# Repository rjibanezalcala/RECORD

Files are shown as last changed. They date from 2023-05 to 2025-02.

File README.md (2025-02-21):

# Welcome to RECORD!
The the REward-COst in Rodent Decision-making (RECORD) is a microcontroller-based system for the design and implementation of behavioural trials with the ability to synchronise with other external neural recording systems. RECORD has a variety of applications, but its main purpose is for behavioural neuroscience implementations.

The system offers modularity and customisability at its core. It includes 3D-printed components, electronics, and software.

[Check out our published paper on Nature Communications Biology!](https://doi.org/10.1038/s42003-024-06489-8)

## 3D printing
We have personally designed every 3D-printed component of the system, and have provided the [AutoCAD files](https://github.com/rjibanezalcala/RECORD/tree/main/3d-prints/cad) for editing, and the [STL files](https://github.com/rjibanezalcala/RECORD/tree/main/3d-prints/stl) for printing directly. 

## Electronic hardware and firmware
The electronics that drive the RECORD system are cheap but effective. We use an embedded systems approach to allow for customisable trials that can either be automated, or performed manually. The embedded electronics work on a command-servicing routine, which will make the electronics react to commands sent by the user via serial communications.

We chose the [Texas Instruments MSP430-FR2355 microcontroller](https://www.ti.com/tool/MSP-EXP430FR2355) due to its low price (~13 USD) and versatility. All of RECORD's [microcontroller firmware](https://github.com/rjibanezalcala/RECORD/tree/main/microcontroller) can be found within this repository.

Our custom-designed PCB is a hub for signals to be relayed from the microcontroller to our rodent arenas. We provide all [Gerber files](https://github.com/rjibanezalcala/RECORD/tree/main/pcb) in this repository.

## Software
Within this repository, you will find example scripts and workflows that can be used as templates for designing your own behavioural trials. For example, we have developed software packages designed specifically for our system. These packages allow scripting of customised trials in [Python](https://github.com/rjibanezalcala/RECORD/tree/main/python). We also provide [Ethovision experiments](https://github.com/rjibanezalcala/RECORD/tree/main/ethovision_experiments) and [Bonsai workflows](https://github.com/rjibanezalcala/RECORD/tree/main/bonsai_workflows) containing our custom decision making task.

Specifically for Ethovision, we provided [Batch scripts](https://github.com/rjibanezalcala/RECORD/tree/main/microcontroller/batch_scripts) that allow communication with our microcontroller system within an experiment's trial-control.

Data management is important for high-throughput systems, thus we created [Serendipity](https://github.com/lddavila/UTEP-Brain-Computation-Lab-Remote-Databases-and-Serendipity-App/tree/main/App%20Deployment%20Folder), a databasing and data pre-processing software suite, provided in an outside repository.

Finally, our data analysis software suite, including [behavioural feature extraction tools](https://github.com/atanugiri/Feature-Extraction), [neuroeconomic analysis tools](https://github.com/rjibanezalcala/RECORD/tree/main/data_analysis/neuroeconomic_analysis), [behavioural classification tools](https://github.com/lddavila/UTEP-Brain-Computation-Lab-Remote-Databases-and-Serendipity-App), are all provided within this and outside repositories.

trial_start_tone was created using [Tonegen](https://www.nch.com.au/tonegen/index.html).

## Documentation

The User Manual, Build guides, and other documentation can be found in our [documentation](https://github.com/rjibanezalcala/RECORD/tree/main/documentation) section.
<!--
> Written with [StackEdit](https://stackedit.io/).
-->
<!--stackedit_data:
eyJoaXN0b3J5IjpbMTIzNTUwMDI1Nl19
-->

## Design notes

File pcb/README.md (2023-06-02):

# Welcome to RECORD/pcb!
Our custom PCB was designed using [Autodesk EAGLE](http://eagle.autodesk.com/). We have provided our projects as a Zip file for importing into EAGLE and making modifications, as well as the Gerber files we used for printing the board. 
## Our custom Printed Circuit Board (PCB)
The printed circuit board serves as a relay center for the various signals that the RECORD hardware needs for function. It also houses various JST connectors to ensure secure connection of the different cable assemblies. Every component on the PCB is through-hole, useful for manual soldering of each component. 
## Resistor values
Resistor values depend mostly on the LEDs chosen for the system. They are mainly for stepping a higher voltage signal down for protection of the LEDs. The voltage divider section is used for protection of the microcontroller, in case input TTL signals cannot be adjusted to the microcontroller's operating range.

> Written with [StackEdit](https://stackedit.io/).
<!--stackedit_data:
eyJoaXN0b3J5IjpbMzA1NjkyMDExLDQxMzA1NjI3NF19
-->

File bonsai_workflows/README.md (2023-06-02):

# Welcome to RECORD/bonsai_workflows!
[Bonsai](https://bonsai-rx.org/) is a visual programming interface that is useful for multiple applications across various fields. Herein, we include the workflows (visual code) we have used for interfacing with [our Basler cameras](https://www.baslerweb.com/en/products/cameras/area-scan-cameras/ace/aca1300-60gc/) for the purpose of tracking an animal's location on the RECORD arenas. 
## Workflow dependencies
This is a list of dependencies that are needed for our workflows. Bolded are the libraries that are absolutely essential. You can install libraries directly from Bonsai using the *Bonsai Gallery*.
1. Bonsai - Core Library
2. Bonsai - Design Library
3. Bonsai - Visualizers Library
4. **Bonsai - Dsp Library**
5. Bonsai - Dsp Design Library
6. Bonsai - Editor
7. **Bonsai - Pylon Library**
8. **Bonsai - Scripting Library**
9. Bonsai - Expression Scripting Library
10. **Bonsai - Starter Pack**
11. **Bonsai - Vision Library** 
12. Bonsai - Vision Design Library
## Basler GigE camera interface
To use Bonsai with a Basler GigE camera, you'll need a software interface that essentially provides Bonsai with the information needed to operate the camera. We recommend Basler's [Pylon Viewer](https://www.baslerweb.com/en/downloads/software-downloads/software-pylon-7-3-0-windows/) for this purpose. After setting up the camera, make sure to export the camera features to a file and feed that to the camera capture node in the "Live rat tracking" workflow contained here.

> Written with [StackEdit](https://stackedit.io/).
<!--stackedit_data:
eyJoaXN0b3J5IjpbLTg0MjU0MDEyM119
-->

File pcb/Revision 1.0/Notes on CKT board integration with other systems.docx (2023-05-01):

### Electrophysiology

### Optogenetics (Behaviour Manipulation)

- Outgoing microcontroller TTL signal was not strong enough to drive both the Prizmatix pulser and the indicator LED (ACK1, SYNC1, ACK2, or SYNC2) circuit.
  - Disconnected LED circuit and the 3.3V TTL was able to drive the pulser.

### Optogenetics (Calcium Imaging)

- The Incopix DAQ box can control the output voltage of its TTLs
  - Set this voltage to 3.3V to avoid damaging the indicator LEDs (ACK1, SYNC1, ACK2, or SYNC2) and microcontroller input.

Raquel Ibáñez Alcalá Created 27 September, 2022 for PCB rev.1.0

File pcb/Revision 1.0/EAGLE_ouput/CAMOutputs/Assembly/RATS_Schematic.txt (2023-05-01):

Partlist exported from R:/Data/Raylene/Documents/EAGLE/projects/FriedmanLab_RATS PCB/RATS_Schematic.sch at 20-Dec-21 21:25

Qty Value             Device            Package                    Parts                                             Description               COPYRIGHT                                                MANUFACTURER_PART_NUMBER MF MFR_NAME MPN OC_FARNELL OC_NEWARK POPULARITY SPICEPREFIX
10                    R-EU_0204/7       0204/7                     R1, R2, R3, R4, R5, R6, R7, R8, R9, R10           RESISTOR, European symbol                                                                                                                        79         R          
12  1N4004            1N4004            DO41-10                    D1, D2, D3, D4, D5, D6, D7, D8, D9, D10, D11, D12 DIODE                                                                                                                                            82                    
4   3.3V              LED5MM            LED5MM                     ACK1, ACK2, SYNC1, SYNC2                          LED                                                                                                                                              93                    
1   ACK1_J            JP1E              JP1                        JP1                                               JUMPER                                                                                                                                           61                    
1   ACK2_J            JP1E              JP1                        JP3                                               JUMPER                                                                                                                                           61                    
4   B2B-XH-A(LF)(SN)  B2B-XH-A(LF)(SN)  CONN_B2B-XH-A(LF)(SN)_JST  TTL/SYNC1, TTL/SYNC2, VALVE_PWR1, VALVE_PWR2                                Copyright (C) 2021 Ultra Librarian. All rights reserved. B2B-XH-A(LF)(SN)            JST                                                     
4   B4B-XH-A_(LF)(SN) B4B-XH-A_(LF)(SN) CONN_B4B-XH-A_(LF)(SN)_JST RELAY_IN1, RELAY_IN2, RELAY_POWER1, RELAY_POWER2                            Copyright (C) 2021 Ultra Librarian. All rights reserved. B4B-XH-A (LF)(SN)           JST                                                     
2   B5B-XH-A(LF)(SN)  B5B-XH-A(LF)(SN)  CONN_B5B-XH-A(LF)(SN)_JST  VALVE_OUT1, VALVE_OUT2                                                      Copyright (C) 2021 Ultra Librarian. All rights reserved. B5B-XH-A(LF)(SN)            JST                                                     
2   B6B-XH-A(LF)(SN)  B6B-XH-A(LF)(SN)  CONN_B6B-XH-A(LF)(SN)_JST  LED_OUT1, LED_OUT2                                                          Copyright (C) 2021 Ultra Librarian. All rights reserved. B6B-XH-A(LF)(SN)            JST                                                     
1   MCU_LED/PWM1      FE05-1            FE05-1                     H5                                                FEMALE HEADER                                                                                                               unknown    unknown   7                     
1   MCU_LED/PWM2      FE05-1            FE05-1                     H6                                                FEMALE HEADER                                                                                                               unknown    unknown   7                     
1   MCU_RELAY         FE08-1            FE08                       H3                                                FEMALE HEADER                                                                                                               unknown    unknown   10                    
1   MCU_TTL           FE05-1            FE05-1                     H2                                                FEMALE HEADER                                                                                                               unknown    unknown   7                     
1   MCU_VCC/GND       FE05-1            FE05-1                     H1                                                FEMALE HEADER                                                                                                               unknown    unknown   7                     
1   RELAY_POWERSEL    JP3Q              JP3Q                       JP5                                               JUMPER                                                                                                                                           5                     
1   RELAY_TRIG        FE10-1            FE10                       H4                                                FEMALE HEADER                                                                                                               unknown    unknown   4                     
1   SYNC1_J           JP1E              JP1                        JP2                                               JUMPER                                                                                                                                           61                    
1   SYNC2_J           JP1E              JP1                        JP4                                               JUMPER                                                                                                                                           61                    
1   VDIVSEL1          JP2E              JP2                        JP6                                               JUMPER                                                                                                                                           34                    
1   VDIVSEL2          JP2E              JP2                        JP7                                               JUMPER                                                                                                                                           34

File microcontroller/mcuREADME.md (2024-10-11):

# Welcome to RECORD/microcontroller!
The code in this repository was written for the [MSP430-FR2355 microcontroller development kit](https://www.ti.com/tool/MSP-EXP430FR2355) in [Texas Instrument's Code Composer Studio 11.1.0](https://www.ti.com/tool/download/CCSTUDIO/11.1.0.00011).

# Firmware
This repository contains 3 files:

 1. 'main.c' file: The microcontroller firmware. This code is essential for the functionality of the microcontroller system and will call the other two files. It contains setup and initialisation, the command servicing routine, interrupt servicing routines, and main variable definitions.
 2. 'RECORD.h' file: A header file containing essential variables and functions necessary for functionality.
 3. 'mcucfg.h' file: A header file referenced by the 'RECORD.h' file that defines default parametres loaded by the microcontroller at startup.
	 - This file contains variables essential to the brightness of the cost lights, as they will control the pulse width-modulated signal that turns on the cost lights.  **Make sure these values are calibrated to your setup's specific needs!**
 
 These three files must be flashed to the microcontroller in order for the RECORD system to work. The 'mcucfg.h' file may be named something else and multiple copies can be made for a setup using multiple RECORD arenas, however, make sure that the 'RECORD.h' file references the correct 'cfg' file when flashing.

## A note on HARP compliance
RECORD firmware is currently not [HARP](https://harp-tech.org/) compliant, however, we are working on this and will be adding HARP compatibility in a future release!

# Updates
A rundown of the current version's most recent changes will be shown here!

## Current version v2.2.0 (17/February/2022) 
### Firmware:
 1. Added the capability to switch TTL operation modes by configuring in configuration mode
	 - TOGGLE will turn the TTL on and keep it on until it is toggled again
	 -  PULSE is the legacy mode, only stays on for as long as TTL_LENGTH
	   indicates, then turns back off. 
	 - OFF is off, duh!
 2. TTL OUT command ‘T’ will now check for the TTL operation mode and act accordingly.
 3. Information mode ('?' command):
	- Will now report the operation mode of the output TTL immediately before reporting CCR values.
	- Will now prompt the user to either enter H to display the help section, or Enter to exit info mode. Any character sent will also exit info mode.
 4. Added command ‘t’ to report the state of the output TTL in text. This is to make sure the state can be reported to serial comm-based systems that are oblivious to I/O signals.
 5. Removed TTL_OUT and ACK from ‘R’ command, so the state of these signals is not altered when doing resets.

> Written with [StackEdit](https://stackedit.io/).
<!--stackedit_data:
eyJoaXN0b3J5IjpbLTU4MTc2NDIxOF19
-->

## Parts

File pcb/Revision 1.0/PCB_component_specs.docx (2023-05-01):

# List of components

PCB Position | Manufacturer | Part Number | Value | Units | Component type
R1* | Sparkfun | COM-10969 | 2.2* ± 5 | kΩ % | Resistor
R2* | Sparkfun | COM-10969 | 3.3* ± 5 | kΩ % | Resistor
R3* | Sparkfun | COM-10969 | 0* | Ω | Resistor
R4* | Sparkfun | COM-10969 | 2.2* ± 5 | kΩ % | Resistor
R5* | Sparkfun | COM-10969 | 3.3* ± 5 | kΩ % | Resistor
R6* | Sparkfun | COM-10969 | 0* | Ω | Resistor
R7* | Sparkfun | COM-10969 | 0* | Ω | Resistor
R8* | Sparkfun | COM-10969 | 0* | Ω | Resistor
R9* | Sparkfun | COM-10969 | 0* | Ω | Resistor
R10* | Sparkfun | COM-10969 | 0* | Ω | Resistor
D1 | Vishay General Semiconductors | 1N4007E-E3/54 | Vf = 1.1 Vr = 1000 | V | Diode
D2 | Vishay General Semiconductors | 1N4007E-E3/54 | Vf = 1.1 Vr = 1000 | V | Diode
D3 | Vishay General Semiconductors | 1N4007E-E3/54 | Vf = 1.1 Vr = 1000 | V | Diode
D4 | Vishay General Semiconductors | 1N4007E-E3/54 | Vf = 1.1 Vr = 1000 | V | Diode
D5 | Vishay General Semiconductors | 1N4007E-E3/54 | Vf = 1.1 Vr = 1000 | V | Diode
D6 | Vishay General Semiconductors | 1N4007E-E3/54 | Vf = 1.1 Vr = 1000 | V | Diode
D7 | Vishay General Semiconductors | 1N4007E-E3/54 | Vf = 1.1 Vr = 1000 | V | Diode
D8 | Vishay General Semiconductors | 1N4007E-E3/54 | Vf = 1.1 Vr = 1000 | V | Diode
D10 | Vishay General Semiconductors | 1N4007E-E3/54 | Vf = 1.1 Vr = 1000 | V | Diode
D11 | Vishay General Semiconductors | 1N4007E-E3/54 | Vf = 1.1 Vr = 1000 | V | Diode
D12 | Vishay General Semiconductors | 1N4007E-E3/54 | Vf = 1.1 Vr = 1000 | V | Diode
H1 | Samtec Inc | TSW-105-07-T-S | Pitch = 2.54 Position = 5 | mm | Board to Board Header
H2 | Samtec Inc | TSW-105-07-T-S | Pitch = 2.54 Position = 5 | mm | Board to Board Header
H3 | Samtec Inc | TSW-108-07-T-S | Pitch = 2.54 Position = 8 | mm | Board to Board Header
H4 | Samtec Inc | TSW-110-07-T-S | Pitch = 2.54 Position = 10 | mm | Board to Board Header
H5 | Samtec Inc | TSW-105-07-T-S | Pitch = 2.54 Position = 5 | mm | Board to Board Header
H6 | Samtec Inc | TSW-105-07-T-S | Pitch = 2.54 Position = 5 | mm | Board to Board Header
JP1 | Samtec Inc | TSW-102-07-T-S | Pitch = 2.54 Position = 2 | mm | Board to Board Header
JP2 | Samtec Inc | TSW-102-07-T-S | Pitch = 2.54 Position = 2 | mm | Board to Board Header
JP3 | Samtec Inc | TSW-102-07-T-S | Pitch = 2.54 Position = 2 | mm | Board to Board Header
JP4 | Samtec Inc | TSW-102-07-T-S | Pitch = 2.54 Position = 2 | mm | Board to Board Header
JP5 | Samtec Inc | TSW-103-07-T-S | Pitch = 2.54 Position = 3 Rows = 2 | mm | Board to Board Header
JP6 | Samtec Inc | TSW-103-07-T-S | Pitch = 2.54 Position = 3 | mm | Board to Board Header
JP7 | Samtec Inc | TSW-103-07-T-S | Pitch = 2.54 Position = 3 | mm | Board to Board Header
CONN1 | Qibaok | XH-6A | Pitch = 2.54 Female Position = 6 | mm | JST-XH Female Header
CONN2 | Qibaok | XH-6A | Pitch = 2.54 Female Position = 6 | mm | JST-XH Female Header
CONN3 | Qibaok | XH-2A | Pitch = 2.54 Female Position = 2 | mm | JST-XH Female Header
CONN4 | Qibaok | XH-2A | Pitch = 2.54 Female Position = 2 | mm | JST-XH Female Header
CONN5 | Qibaok | XH-5A | Pitch = 2.54 Female Position = 5 | mm | JST-XH Female Header
CONN6 | Qibaok | XH-5A | Pitch = 2.54 Female Position = 5 | mm | JST-XH Female Header
CONN7 | Qibaok | XH-4A | Pitch = 2.54 Female Position = 4 | mm | JST-XH Female Header
CONN8 | Qibaok | XH-4A | Pitch = 2.54 Female Position = 4 | mm | JST-XH Female Header
CONN9 | Qibaok | XH-4A | Pitch = 2.54 Female Position = 4 | mm | JST-XH Female Header
CONN10 | Qibaok | XH-4A | Pitch = 2.54 Female Position = 4 | mm | JST-XH Female Header
CONN11 | Qibaok | XH-2A | Pitch = 2.54 Female Position = 2 | mm | JST-XH Female Header
CONN12 | Qibaok | XH-2A | Pitch = 2.54 Female Position = 2 | mm | JST-XH Female Header
SYNC1* | Kingbright Company LLC | WP7113VBC/D | Vf = 3.3** Lens = 5 | V mm | Light Emitting Diode (LED)
ACK1* | Kingbright Company LLC | WP7113VBC/D | Vf = 3.3** Lens = 5 | V mm | Light Emitting Diode (LED)
SYNC2* | Kingbright Company LLC | WP7113VBC/D | Vf = 3.3** Lens = 5 | V mm | Light Emitting Diode (LED)
ACK2* | Kingbright Company LLC | WP7113VBC/D | Vf = 3.3** Lens = 5 | V mm | Light Emitting Diode (LED)

* Components and values reflect what was used for our particular setup. These Values should be chosen according to each system’s requirements

** Different LED forward voltages may be needed depending on each individual system. The LED should be able to turn on with its corresponding TTL signal voltages delivered by the microcontroller and voltage divider output. Voltage divider output is dependent on R1, R2, and R3 for SYNC1 and ACK1, as well as R4, R5, and R6 for SYNC2 and ACK2. Value shown is the typical operating voltage for the LED, see component datasheet for maximum and minimum forward voltages.

Internal Connectors:

CONN7 | Qibaok | XH-4Y | Pitch = 2.54 Male Position = 4 | mm | JST-XH Male Connector
CONN8 | Qibaok | XH-4Y | Pitch = 2.54 Male Position = 4 | mm | JST-XH Male Connector
CONN9 | Qibaok | XH-4Y | Pitch = 2.54 Male Position = 4 | mm | JST-XH Male Connector
CONN10 | Qibaok | XH-4Y | Pitch = 2.54 Male Position = 4 | mm | JST-XH Male Connector

# Microcontroller, Relay, and PCB Connections

### Connections for MCU 1

Signal | Position on MCU (MSP430-FR2355) | Position on PCB | Position on Relay Shield
Cost LED1 | P6.0 | H5.1 | -
Cost LED2 | P6.1 | H5.2 | -
Cost LED3 | P6.2 | H5.3 | -
Cost LED4 | P6.3 | H5.4 | -
Trial Indicator LED | P6.4 | H5.5 | -
Low-Voltage Supply* | 3V3 or 5V* | H1.1 | -
Ground | GND | H1.2 | -
SYNC | P3.5 or P3.6*** | H2.1 | -
ACK | P3.0*** | H2.2 | -
Trigger Signal for Relay 1 | P3.1 | H3.1 | -
Trigger Signal for Relay 2 | P3.2 | H3.2 | -
Trigger Signal for Relay 3 | P3.7 | H3.3 | -
Trigger Signal for Relay 4 | P3.4 | H3.4 | -
MCU to Relay 1 | - | H4.1 | IN1
MCU to Relay 2 | - | H4.2 | IN2
MCU to Relay 3 | - | H4.3 | IN3
MCU to Relay 4 | - | H4.4 | IN4
Relay VCC | - | H4.9 | VCC
Relay GND | - | H4.10 | GND
Relay 1 to Valve 1 | - | CONN7.1 | Relay 1, Normally Open Terminal
Relay 2 to Valve 2 | - | CONN7.2 | Relay 2, Normally Open Terminal
Relay 3 to Valve 3 | - | CONN7.3 | Relay 3, Normally Open Terminal
Relay 4 to Valve 4 | - | CONN7.4 | Relay 4, Normally Open Terminal
Common High-voltage supply for valves 1 - 4 | - | CONN9.1-4** | Relay 1-4, COM Terminal

* Supplying low-voltage power to the PCB serves to route the voltage and ground to the relay shield. Make sure you are providing enough power to the relay shield and that the jumpers on JP5 are configured in the correct way to carry that voltage. The relay shield may be able to operate on 3.3V, however 5V is recommended.

** Connector 9 simply supplies voltage to the relay. The COM terminal is shorted with the Normally Open terminal when the relay is activated. The order in which the pins on the connector are connected to each relay’s COM terminal has no effect on the function of the system.

*** This connection depends on the particular use-case scenario. P3.0 is the outgoing ACK signal that pulses every time a command is executed, P3.5 is an user-triggerable outgoing TTL signal, and P3.6 is for incoming TTL signals. Incoming TTL signals must be stepped down to 3.3V to not damage the system. Care must be taken when selecting what should be connected where.

### Connections for MCU 2

Signal | Position on MCU | Position on PCB | Position on Relay Shield
Cost LED1 | P6.0 | H6.1 | -
Cost LED2 | P6.1 | H6.2 | -
Cost LED3 | P6.2 | H6.3 | -
Cost LED4 | P6.3 | H6.4 | -
Trial Indicator LED | P6.4 | H6.5 | -
Low-Voltage Supply* | 3V3 or 5V* | H1.3 | -
Ground | GND | H1.4 | -
SYNC | P3.5 or P3.6*** | H2.4 | -
ACK | P3.0*** | H2.5 | -
Trigger Signal for Relay 1 | P3.1 | H3.5 | -
Trigger Signal for Relay 2 | P3.2 | H3.6 | -
Trigger Signal for Relay 3 | P3.7 | H3.7 | -
Trigger Signal for Relay 4 | P3.4 | H3.8 | -
MCU to Relay 1 | - | H4.5 | IN5
MCU to Relay 2 | - | H4.6 | IN6
MCU to Relay 3 | - | H4.7 | IN7
MCU to Relay 4 | - | H4.8 | IN8
Relay VCC | - | H4.9 | VCC
Relay GND | - | H4.10 | GND
Relay 5 to Valve 1 | - | CONN8.1 | Relay 5, Normally Open Terminal
Relay 6 to Valve 2 | - | CONN8.2 | Relay 6, Normally Open Terminal
Relay 7 to Valve 3 | - | CONN8.3 | Relay 7, Normally Open Terminal
Relay 8 to Valve 4 | - | CONN8.4 | Relay 8, Normally Open Terminal
Common High-voltage supply for valves 1 - 4 | - | CONN10.1-4** | Relay 5-8, COM Terminal

* Supplying low-voltage power to the PCB serves to route the voltage and ground to the relay shield. Make sure you are providing enough power to the relay shield and that the jumpers on JP5 are configured in the correct way to carry that voltage. The relay shield may be able to operate on 3.3V, however 5V is recommended.

** Connector 10 simply supplies voltage to the relay. The COM terminal is shorted with the Normally Open terminal when the relay is activated. The order in which the pins on the connector are connected to each relay’s COM terminal has no effect on the function of the system.

*** This connection depends on the particular use-case scenario. P3.0 is the outgoing ACK signal that pulses every time a command is executed, P3.5 is an user-triggerable outgoing TTL signal, and P3.6 is for incoming TTL signals. Incoming TTL signals must be stepped down to 3.3V to not damage the system.

Revision 1.1 PCB Revision 1.0

Documentation and design by Raquel Ibáñez Alcalá Created 25/January/2022, last updated 25/August/2022 (Rev. 1.1) PCB Rev. 1.0

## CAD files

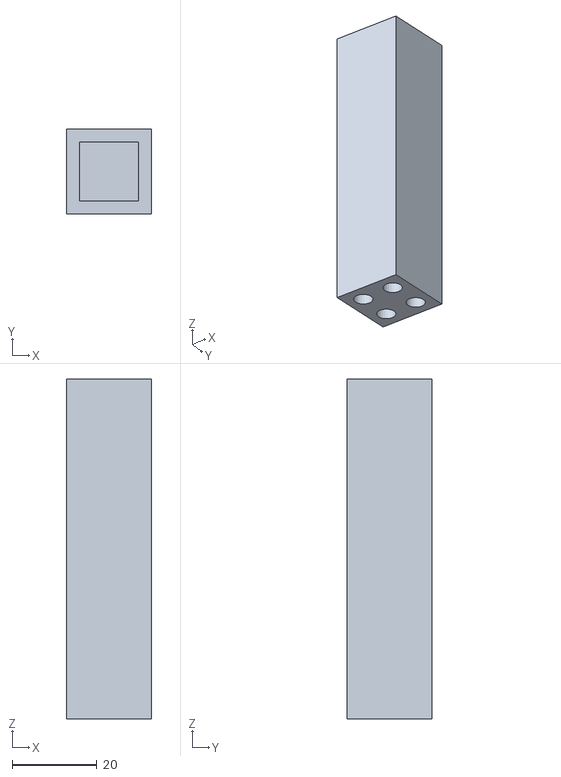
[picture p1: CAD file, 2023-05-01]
3d-prints/stl/Basic Pillar v2.1.stl
20.0 x 20.0 x 80.0

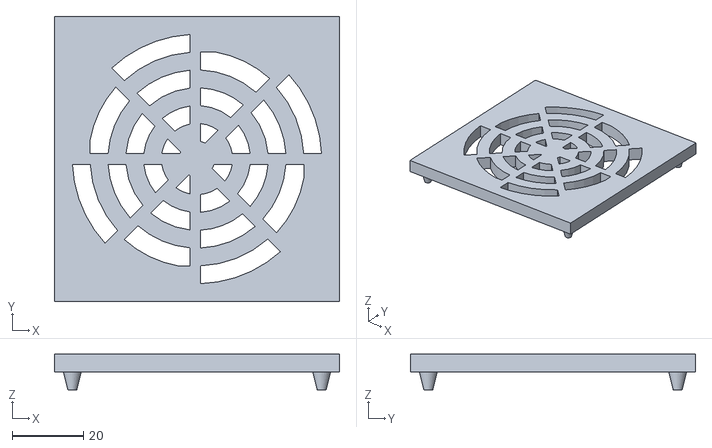
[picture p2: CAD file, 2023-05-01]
3d-prints/stl/Radial Floor Tile.stl
80.0 x 80.0 x 10.00

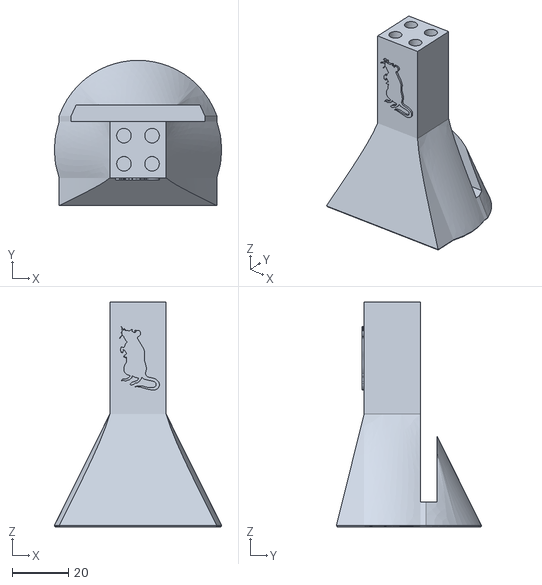
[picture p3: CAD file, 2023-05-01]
3d-prints/stl/Wall Support Pillar v2.0.stl
59.6 x 51.7 x 80.0

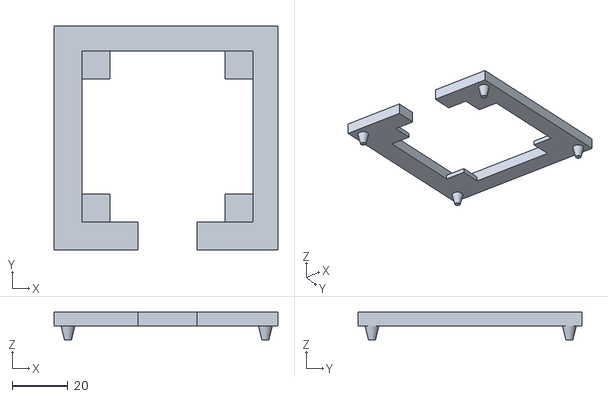
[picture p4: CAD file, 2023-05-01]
3d-prints/stl/Feeder Base Tile.stl
80.0 x 80.0 x 10.00

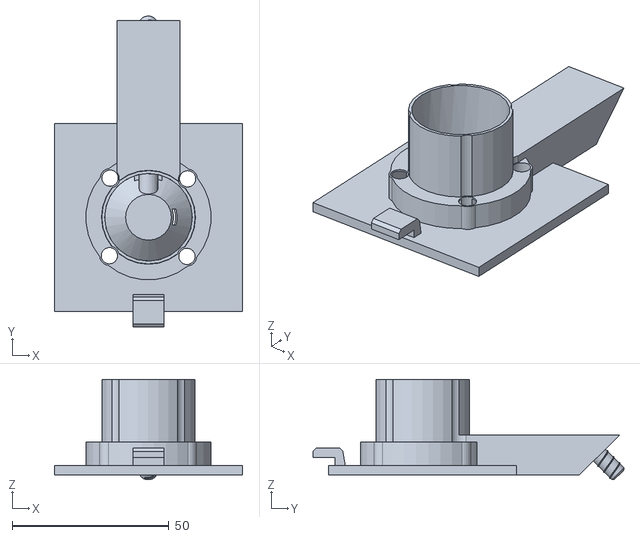
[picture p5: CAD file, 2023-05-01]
3d-prints/stl/Feeder v1.9.9.stl
60.0 x 99.2 x 32.1

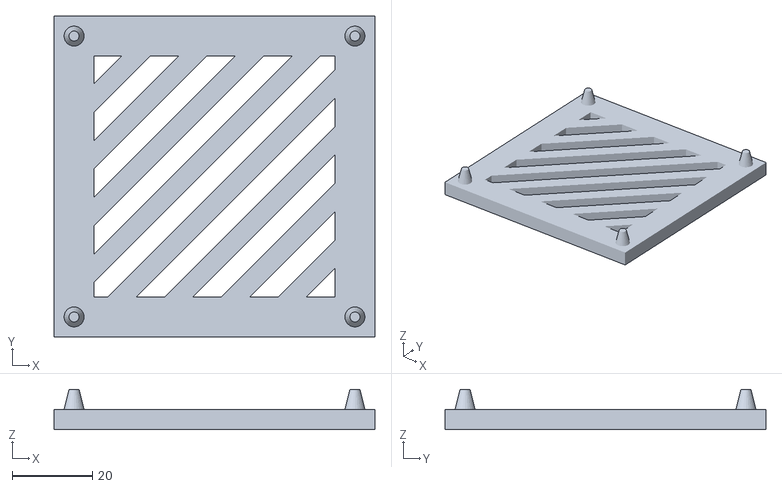
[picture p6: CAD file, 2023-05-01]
3d-prints/stl/Diagonal Floor Tile.stl
80.0 x 80.0 x 10.00

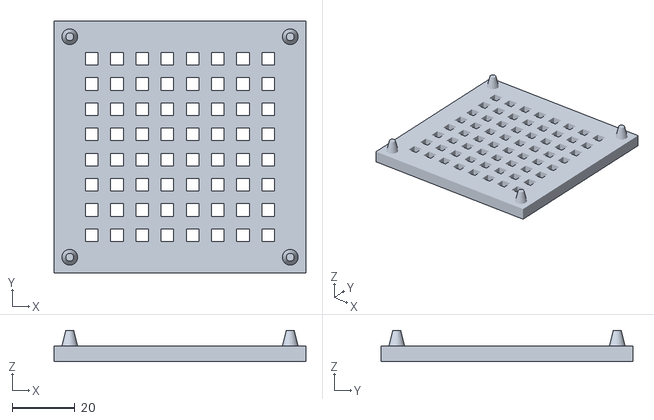
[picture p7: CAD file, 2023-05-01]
3d-prints/stl/Grid Floor Tile.stl
80.0 x 80.0 x 10.00

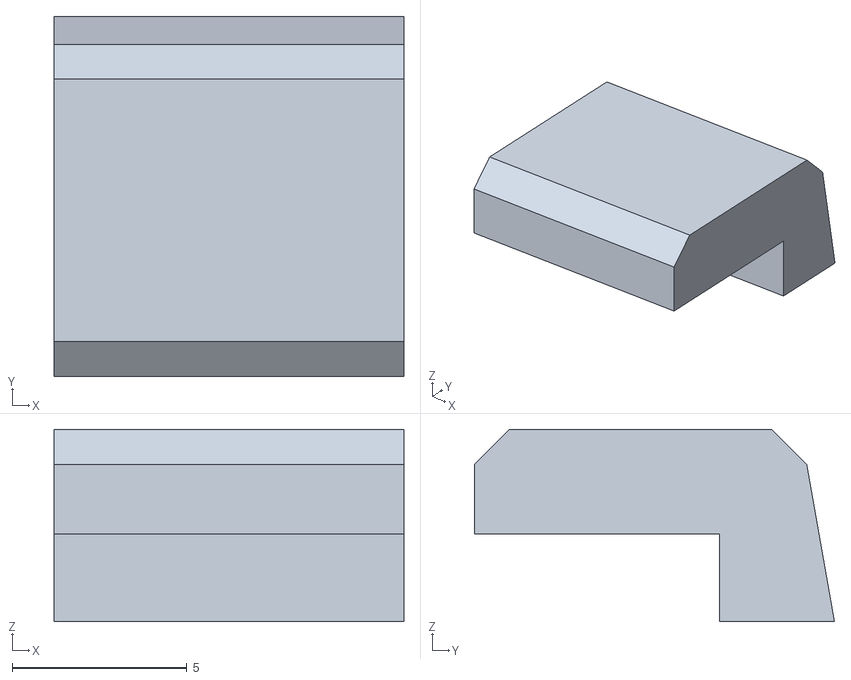
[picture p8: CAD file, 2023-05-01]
3d-prints/stl/Front Leg for Feeder v1.9.8.stl
10.0 x 10.3 x 5.50

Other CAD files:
3d-prints/cad/Feeder Base Tile DWG.dwg
3d-prints/cad/Overhead LED Holder DWG.dwg
3d-prints/cad/Basic Pillar v2.1 DWG.dwg
3d-prints/cad/Radial Floor Tile DWG.dwg
3d-prints/cad/Horizontal Floor Tile DWG.dwg
3d-prints/cad/Diagonal Floor Tile DWG.dwg
3d-prints/cad/Feeder v1.9.9 DWG.dwg
3d-prints/cad/Grid Floor Tile DWG.dwg
3d-prints/stl/Horizontal Floor Tile.stl
3d-prints/cad/Wall Support Pillar DWG v2.0.dwg
3d-prints/stl/Overhead LED Holder.stl

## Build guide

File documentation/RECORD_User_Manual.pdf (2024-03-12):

Written by Raquel Ibáñez Alcalá Device: Texas Instruments MSP430-FR2355 development board running RECORD Firmware Created 8/May/2023, last updated 12/Mar/2024 (Rev. 1.2)

R.E.C.O.R.D.

(Reward-Cost in Rodent Decision-making)

# User Manual

Revision 1.1

(Rev. 1.2)

## Table of Contents

How to upload/update Firmware on a Texas Instrument Microcontroller Dev. Board........ 29

# Background information

This guide will talk specifically about the Texas Instruments MSP-EXP430FR2355 launchpad development kit (https://www.ti.com/tool/MSP-EXP430FR2355) and about microcontroller features specific to the RECORD system. Pin numbers, peripherals, and connections will differ between microcontrollers from the same and different manufacturers, and we cannot guarantee that this guide will be accurate for any other microcontroller. For a detailed user guide on this microcontroller, please see the manufacturer user guide (https://www.ti.com/lit/ug/slau445i/slau445i.pdf?ts=1683549586584) ((https://www.ti.com/product/MSP430FR2355).

## How LED brightness is controlled

The RECORD system microcontroller uses Pulse Width Modulation (PWM) to regulate the brightness of the LEDs which encode cost levels. A total of four PWM signals are produced by the microcontroller, one for each feeder. The amount of time within the PWM signal’s period that the signal is on (logical high) is defined as the duty cycle. A higher duty cycle will result in a brighter LED, while a lower duty cycle will result in a dimmer LED. The duty cycle is dependent on two Capture/Compare Register (CCR) values; CCR0 and CCR1, which are defined in the microcontroller firmware.

The duty cycle is defined by the formula:

DC(%) = 1 − | , on time
signal period

where signal period is the length of time it takes for the signal to complete a full cycle, and on time is the amount of time the signal is held at a logical high. We can expand this formula to be in terms of our two CCR values:
DC(%) = 1 − ,

CCR1
CCR0

Where CCR0 defines how many ticks it will take to count up to the signal’s period and sets the signal to a logical high, and CCR1 is how many ticks it takes to bring the signal back down to logical 0.

To explain ticks, we must first talk about the microcontroller’s internal clock. The microcontroller chip runs at a certain speed determined by an internal clock, which is driven by a crystal oscillator. In the RECORD system, the oscillator signal is internally divided and fed to the system clock, which produces an 8 MHz clock signal, this is set as the system clock. Each cycle in the system clock signal is defined as a tick.

With the system clock set to a frequency of 8MHz, we can define the period of the PWM signal as 1 millisecond by setting CCR0 to a value of 8000. We determine this value by using the formula:

CCR0 =

Desired PWM period
Clock period
We want a PWM period of 1 millisecond since this value is relatively easy to work with, so plugging the values in , we get:
CCR0 = | .

0.001
8,000,000

−1 = 8000

CCR1 is a similar but user-variable value which defines the amount of ticks it should take for the signal to be set to a logical low. This in turn defines the width of the signal pulse. As CCR1 approaches CCR0, the width of the pulse will increase, making the LED glow brighter, as CCR1 approaches 0 the shorter the pulse will be and the dimmer the LED will glow. Since CCR1 is the only parameter that can be adjusted, we will refer to it only as the CCR value. Thus, the driving factor in regulating the cost intensity is the CCR value, a whole number ranging from 0 to a maximum of 8000.

In summary, the brightness of the cost LED can be controlled by varying how long in the signal period the signal is kept at logical high vs logical low. This is defined as the duty cycle of the PWM signal. The rest of this guide will be referencing the CCR value for instructions.

Lastly, we must relate LED brightness (Lux) to the CCR value. It is also important to relate these two parameters to the duty cycle of the PWM signal, as the brightness of the cost LED will be dependent on the shape of the PWM signal and not voltage. We do this in our cost LED calibration document, linked below:

LED Calibration Data - Google Sheets (https://docs.google.com/spreadsheets/d/1rNoFZjvHOEHzDgk6kuDBNOS2BQlJQwXVIH6rNtAQolY/edit)

## What are cost levels?

Cost levels are discrete brightness levels that the microcontroller can set. As mentioned before, cost levels are dictated by the CCR value. It is important to note that the CCR value and LED brightness have an inverse relationship, meaning that as the CCR value approaches its maximum of 8000, the LED brightness will approach 0, or the LED will be dimmer until it turns off. Cost levels are measured in Lux, which is a distance-dependent brightness unit measured using a lightmeter. We typically measure Lux at 3 mm or less away from the LEDs. Each cost level is calibrated to a range of Lux values. In rodents, bright light induces an aversive reaction, which is why light was chosen to serve as a cost in our cost/benefit tasks. Brightness requirements may change from rat to rat, for this reason, it is important to calibrate!

The following are general guidelines of how many Lux are required for each cost level. Always check with your section supervisor or the PI before determining what is needed at each level.

- Cost level 0 (L0, 0 Lux) represents an LED which is off. This presents no cost to the rat in the arena. It is typically not used in an experiment setting outside of simply turning lights off, though some special cases may apply. This level is not configurable.

- Cost level 1 (L1, 7-15 Lux) corresponds to the lowest brightness . This presents a low cost for the rat in the arena to obtain its reward. We typically keep this level low enough to not scare a rat, but high enough for them to see the light.
- Cost level 2 (L2, 40-60 Lux) corresponds to an intermediate brightness between the lowest and highest. It is associated with a mid-level cost. This level should be high enough to be somewhat uncomfortable, but not so bright that the rat never approaches offers associated with this cost.
- Finally, cost level 3 (L3, 140-? Lux) corresponds to the highest (safe) brightness for our experiments. The highest Lux that an LED can output will depend on the LED itself, but it should never shine so bright that the rat is traumatised by it and becomes conditioned to hate running our experiments.

Cost levels are calibrated using the program PuTTY, which has a command line analogue called Plink. This guide has a section on using PuTTY to explain how calibration and reconfiguration is done, as its graphical user interface is somewhat friendlier for the average user.

## What are reward levels?

Reward levels are not so much dictated by the microcontroller, but rather the rewards made available on the RECORD arenas. However, the microcontroller sees reward levels as the relay which activates the solenoid valve that dispenses a reward to a particular feeder, thus it is extremely important that each solenoid valve and feeder is associated with the correct relay port. When it comes to reward, the only thing the microcontroller can do is select a particular feeder to dispense reward to, and hold a relay closed for a set amount of time so that the solenoid valve dispenses more or less solution into a feeder (see ”Configuring relay active time”).

# Communicating with the RECORD microcontrollers

## Using PuTTY to communicate with RECORD

PuTTY is an SSH/Telnet client which also has the capability to serve as a serial communications interface between a PC and a serial device connected through a USB COM port, such as a microcontroller running the Universal Asynchronous Receive Transmit (UART) protocol. In other words, you use PuTTY to communicate to the RECORD system microcontrollers while they are connected via USB cable to a PC. Multiple PuTTY sessions may be loaded at the same time to communicate with each microcontroller, but two sessions cannot communicate with the same microcontroller. This section will walk you through how to go through the process of calibrating each feeder to a desired lux level.

This guide assumes a Windows PC with Code Composer Studio (https://www.ti.com/tool/CCSTUDIO) and PuTTY (https://www.putty.org/) already installed is being used, and that a microcontroller running firmware version v1.2 or later has been plugged into your PC.

### Setting PuTTY up for the first time

1. On the RECORD microcontroller, make sure that the top RXD and TXD pins on the top board-to-board header are jumped to P1.6 and P1.7, respectively.
2. Connect the RECORD microcontroller to your computer via USB.
3. On Windows, open the device manager by pressing and holding the Window key and pressing the ‘R’ (‘Run’) key to open the run dialog. Type ‘devmgmt.msc’ into the dialog box and press Enter.

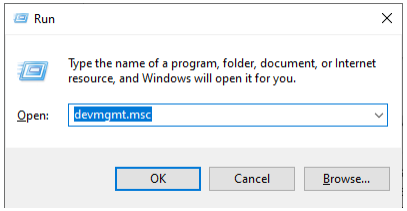
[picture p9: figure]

4. Navigate down to ‘Ports (COM & LPT)’ and expand the dropdown menu. Look for ‘MSP Application UART1’ and take note of the COM port number listed here (in parenthesis). If you do not see this entry, make sure that you have Code Composer Studio with the MSP430 library and drivers installed in your system
(https://www.ti.com/tool/CCSTUDIO).

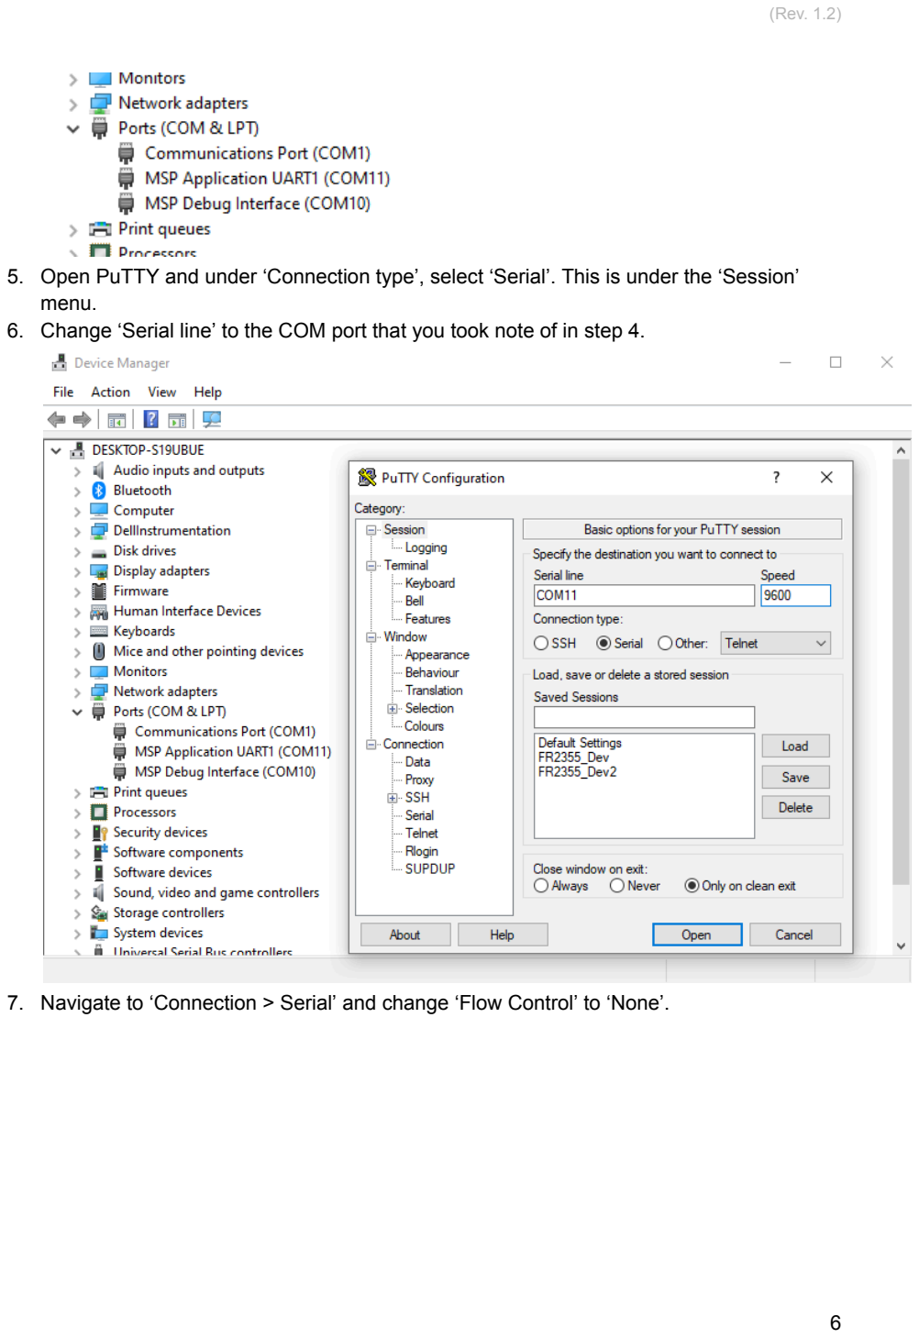
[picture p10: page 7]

5. Open PuTTY and under ‘Connection type’, select ‘Serial’. This is under the ‘Session’ menu.
6. Change ‘Serial line’ to the COM port that you took note of in step 4.
7. Navigate to ‘Connection > Serial’ and change ‘Flow Control’ to ‘None’.

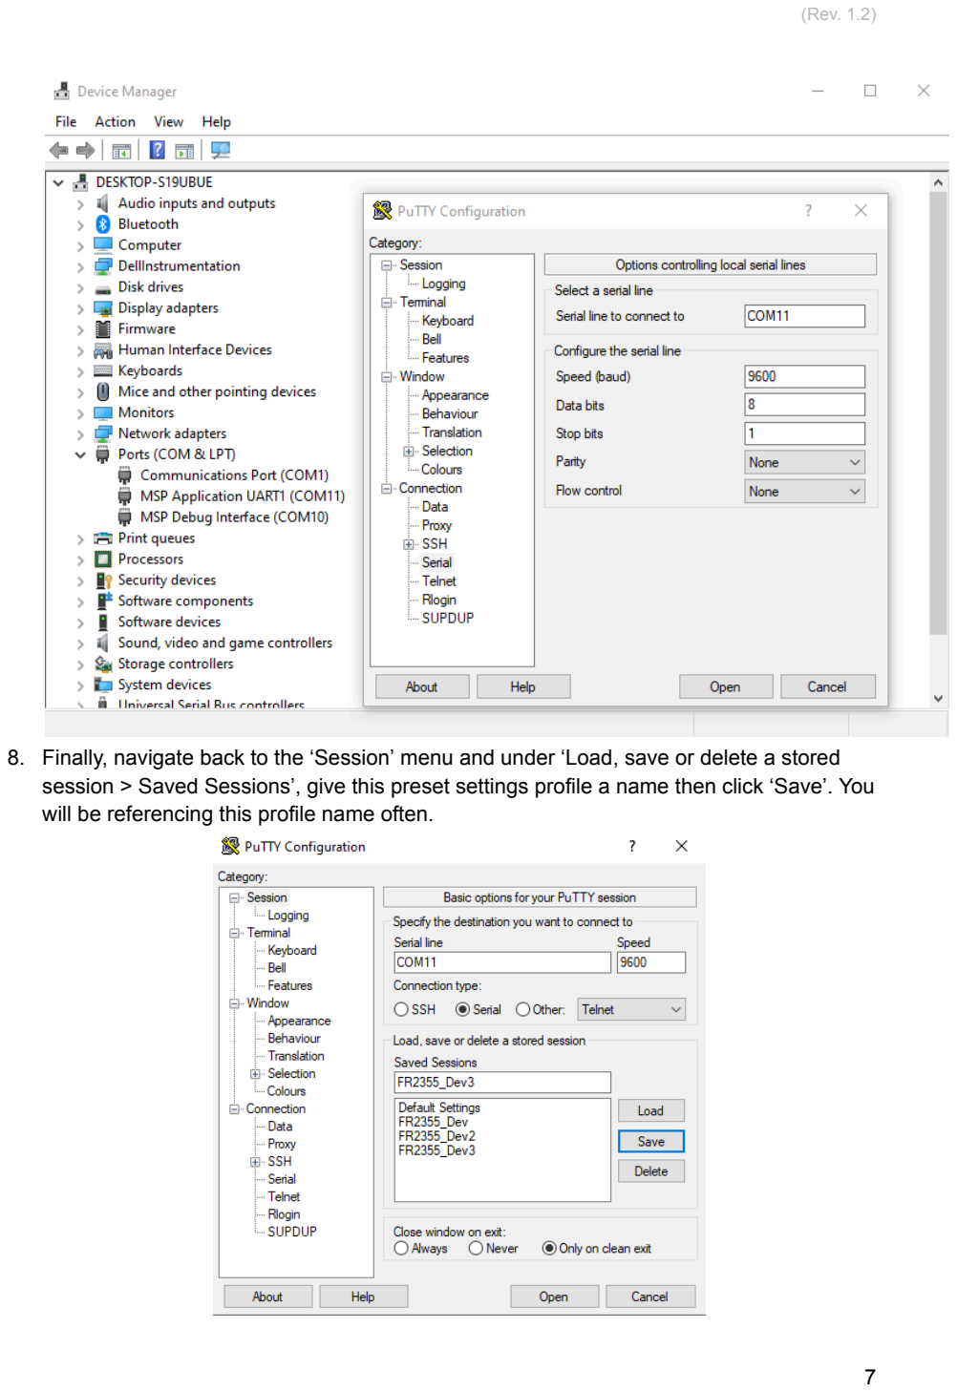
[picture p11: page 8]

8. Finally, navigate back to the ‘Session’ menu and under ‘Load, save or delete a stored session > Saved Sessions’, give this preset settings profile a name then click ‘Save’. You will be referencing this profile name often.

9. Click ‘Open’ and a black command window should appear. Try sending a capital ‘R’ (‘Reset’) to see if the device responds.

### Opening PuTTY and connecting to an arena microcontroller

1. Turn on the microcontrollers. Do so by connecting them to the PC via USB. In our case at the Friedman Lab, do so by pressing the rightmost button on the USB hub located to the left of the computer tower in the recording room. The USB hub will light up with blue light indicating that it is on.
2. Open PuTTY. You will likely find this program in a folder named “PuTTY (64-bit)” under the Windows Start menu. Otherwise, you may search for it by typing “putty” in the Windows search bar.
3. Once open, PuTTY will load a default session preset. Near the bottom you will find a white space containing other session presets, and at the very bottom of the windows, you’ll find an “Open” button. DO NOT click the “Open” button yet!

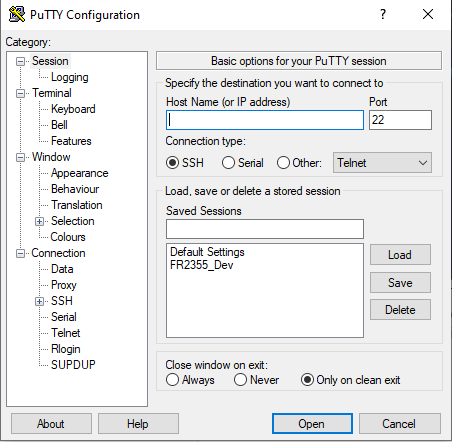
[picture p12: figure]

4. Each preset will configure PuTTY to work with its corresponding arena. Double click the preset that corresponds to the arena that you are calibrating, this will open a communication channel to that arena’s microcontroller.
a. FR2355 - Arena 1
b. FR2355_2 - Arena 2
c. FR2355_3 - Arena 3
d. FR2355_4 - Arena 4

5. A small black window with a green cursor and no text will appear. This is where commands are sent to the microcontroller. With the window in focus, type the letter ‘R’ (capitalised). The microcontroller will respond by repeating what you sent, along with a message, which will change depending on what you send. ‘R’ is a command that resets the microcontroller to its idle state, turning all LEDs off. The black PuTTY window should now display the message “all off”; if no message is displayed, make sure the microcontroller is powered and connected to the PC, then repeat steps 2 through 4 and try again. Contact a lab supervisor or the PI if there is still no response, DO NOT tamper with the microcontroller on your own.
6. You’ve successfully connected and are now communicating with the microcontroller! Continue to the next section to calibrate or configure LED brightness.

### Using Plink to communicate with RECORD

RECORD can be controlled via command prompt if Plink, PuTTY’s command line executable, is installed. Once a PuTTY session is created following the steps in the previous two sections, one may opt to interfacing with the system by opening a command line window and typing
plink -load [session name],
After which the command line will behave just the same as any PuTTY command line.

## Using RECORD-lib to communicate with RECORD

RECORD-lib is a Python (https://www.python.org/) library custom made for communications with the RECORD system. It uses the ‘pyserial’ library as a basis and includes various functions to do things like set a cost light up, deliver a reward, etc. This along with the ‘Trials’ class was used to create a Python script that can be run through a command line interface or through an IDE like Spyder (https://www.spyder-ide.org/) which runs through our high- and low-cost cost/benefit tasks, as well as our association task through tweaking of a few parameters. You can find RECORD-lib in our Github repository (https://github.com/rjibanezalcala/RECORD/tree/main/python/RECORD-lib) along with our sample trial
(https://github.com/rjibanezalcala/RECORD/blob/main/python/RECORD-lib/sample_trial_with_output_v0.3.5.py). (https://github.com/rjibanezalcala/RECORD/blob/main/python/RECORD-lib/sample_trial_with_output_v0.3.5.py) Here we’ll describe what each parameter is.

Currently, the following trial parameters must be modified in the code itself, so a graphical IDE is recommended when running trials. After all parameters have been set, click the ‘Run’ button or press ‘F5’ to run the script.

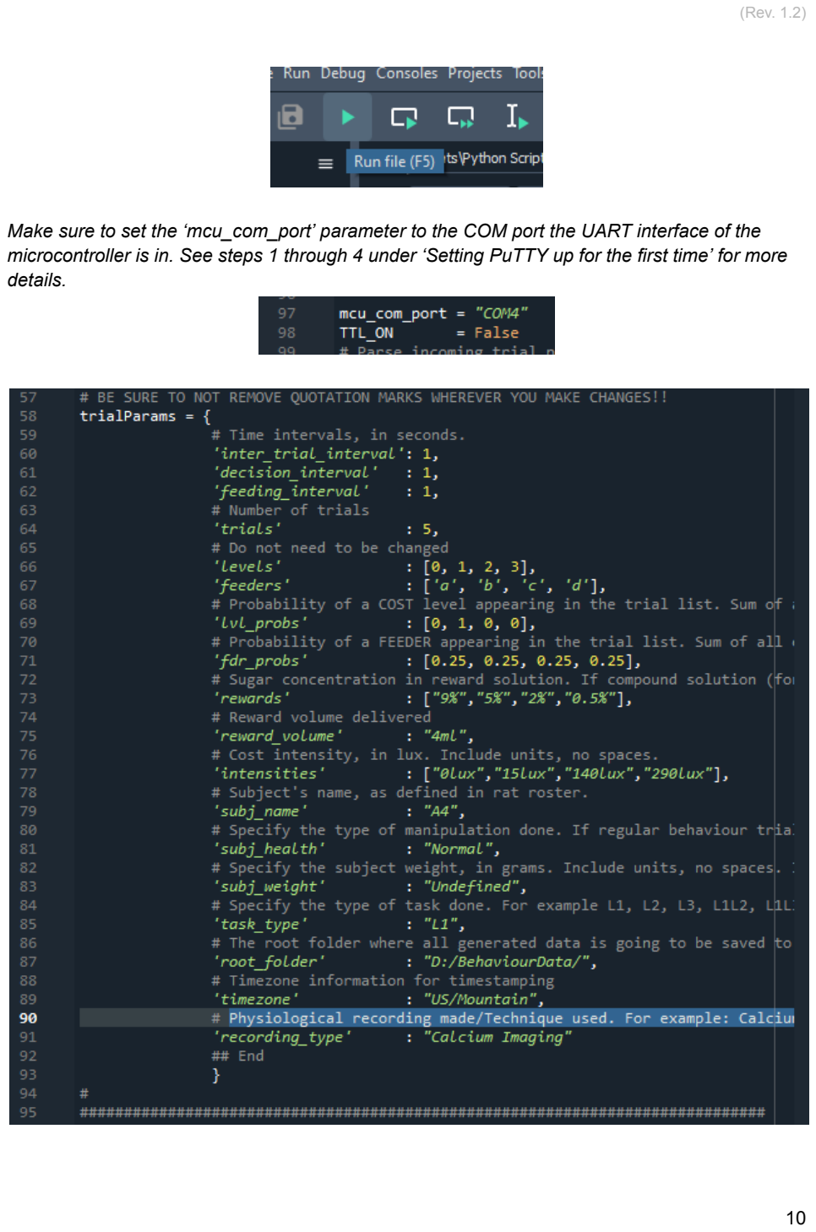
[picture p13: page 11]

Make sure to set the ‘mcu_com_port’ parameter to the COM port the UART interface of the microcontroller is in. See steps 1 through 4 under ‘Setting PuTTY up for the first time’ for more details.

Parameter | Description | Example
inter_trial_interval | The time delay in-between trials. | 5
decision_interval | The time delay between when an offer is presented and when it is decided if a subject approached the offer. | 3
feeding_interval | The time delay to allow the subject to consume the reward. | 5
trials | The number of trials in a session | 40
levels | A list of the available cost levels in the trials, from lowest cost level at element 0, to the highest cost level at element N-1 (typically N= 4). | [0, 1, 2, 3]
feeders | A list of the available feeders representing reward levels in the trials, from the first feeder with the highest reward level at element 0, to the last feeder with the lowest reward level at element N-1 (typically N= 4). | [1, 2, 3, 4]
lvl_probs | Probability of a COST level appearing in the trial list. Cost level 0 is represented in element 0, and the highest cost level is represented in element N-1 (typically N= 4). Sum of all elements must equal 1. | [0, 0.5, 0, 0.5] (represents an L1 L3 trial)
fdr_probs | Probability of a FEEDER appearing in the trial list. Feeder 1 is represented in element 0, and the last feeder is represented in element N-1 (typically N= 4). | [0.25, 0.25, 0.25, 0.25]

| Sum of all elements must equal 1.
rewards | Sugar concentration in each reward solution. If compound solution (for example sucrose + alcohol), include second solute concentration in parenthesis: X%(Y%). No spaces. Serves as a label for the data. | ["9%","5%","2%","0.5%"]
reward_volume | Reward volume delivered. Does not affect the reward volume delivered by RECORD, serves only as a data label. | “4ml”
intensities | Cost intensity, in lux. Including units, no spaces. Does not affect the LED brightness delivered by RECORD, serves only as a data label. | ["0lux","15lux","140lux","290lu x"]
subj_name | Subject's name or ID number, as defined in rat roster. | “Princess”
subj_health | Specifies the type of manipulation done. If regular behaviour trial: "Normal"; if alcohol trial: "Alcohol"; if oxy trial: "Oxycodone"; etc... | “Normal”
subj_weight | Specify the subject weight, in grams. Include units, no spaces. If no weight is defined, write "Undefined" | “200 g”
task_type | Specify the type of task done. For example L1, L2, L3, L1L2, L1L3, etc. | “L1L3”
root_folder | The root folder where all generated data is going to be saved to. Can be an absolute or relative path. | "D:/BehaviourData/"

timezone | Timezone information for timestamp data. If not defined, defaults to UTC. We use the ‘pytz’ library to generate timezone data on our ‘datetime’ timestamps. | “US/Mountain”
recording_type | Physiological recording made/Technique used. For example: Calcium Imaging, Optogenetics, Electrophysiology, etc. | “Calcium Imaging”

# RECORD System Operation

The RECORD system consists of the arenas and its individual components, but of equal importance, the microcontroller unit and the various electronic components that surround it. This section will use PuTTY to demonstrate the operation of the system, but the RECORD system can also be operated via batch script or via Python script using the RECORD-lib package (https://github.com/rjibanezalcala/RECORD/tree/main/python/RECORD-lib).

## Available Commands

Command | Description
# | Turns on a specific feeder LED ring at a specified level. The microcontroller will quietly wait for an input and only execute it once four characters have been entered. The second and fourth character dictate the feeder that will be activated and the cost level at which the light will be turned on. Generally, it is recommended that inputs are formatted in the following way: FxLy, where X is the feeder, and Y is the cost level.

F, G, H, and J | Toggles relay 1, 2, 3, and 4, respectively, which will open and close their respective valves. The amount of time that the relay will be closed can be configured in configuration mode.
R | Resets everything but the TTL signals. All LEDs are turned off and relays are opened.
$ | Starts configuration mode. Instructions will pop up as soon as you input this command. This will allow you to reconfigure how bright feeder LEDs should be, how long valves stay open, how long TTL pulses are, amongst other settings. *
% | Starts calibration mode. This allows the user to increase and decrease the brightness of the cost LEDs on the fly. It is recommended this command is only used to calibrate the LED brightness of each cost level and not during a trial. *
T | Sends a TTL out through port 3.6. *
K | Toggles the 'trial in progress' light.
Q | Starts the internal timer. This timer counts seconds and milliseconds. Starting the timer will increment the timestamps that show in the acknowledgement message for each command.

W | Gets the current time from the internal timer. Time will be formatted as [seconds].[milliseconds].
E | Stops the internal timer. This will reset the timer back to 0.
Y | Allows the system to respond to external TTLs received through P3.5.
? | Shows system information and a list of available commands with a description of each. *

* All commands (with the exception of 'T', ‘$’, ‘%’, and ‘?’) will be acknowledged with the ACK signal through port 3.0 upon execution

## The internal timer

An internal timer can be used to keep track of events that happen throughout a trial. Here, each event refers to each time an event is sent to and acknowledged by the microcontroller. In each acknowledgement message, a timestamp will be reported from the internal timer; if the timer has not been started, the timestamp reported will read “0.0”.

## Requesting system information

When requesting system information via the ‘?’ command, relevant information will be displayed first, then if a command list is needed, the user can then send an ‘H’ character. Entering any other character (including a return character) will exit the command.

## The microcontroller buttons

The onboard microcontroller buttons serve only as a test to determine if the microcontroller is receiving commands. They currently (firmware v2.2.0) serve no other purpose.

# Configuration mode

This mode’s main purpose is to set the system up with different operating conditions for a customisable setup, when changes need to be made on the fly. However, it is important to note that any changes made in configuration mode will be lost as soon as the microcontroller is power cycled, as it will boot up with the default parameters set up by the “_cfg.h” file in the microcontroller firmware
(https://github.com/rjibanezalcala/RECORD/blob/main/microcontroller/mcucfg_dev1.h). To make changes to the default configuration of the device, the microcontroller must be re-flashed with the desired changes.

When no other commands are active, configuration mode is accessed via the ‘$’ command. It is recommended that this mode be accessed through a command line interface such as PuTTY or Plink, but configuration can be scripted through any scripting language, or through RECORD-lib, our python library (https://github.com/rjibanezalcala/RECORD/tree/main/python/RECORD-lib).

## Configuring LED brightness

Configuring the brightness at which the LEDs turn on at each cost level is done by selecting option ‘A’ after entering configuration mode. The microcontroller will then prompt the user for some input, namely…
1. What feeder needs to be configured,
2. What cost level is to be configured,
3. And the new CCR value (see more on CCR values under the “How LED brightness is controlled” section).

## Configuring relay active time

How long the relays are held open when using the F, G, H, or J commands is option ‘B’ after entering configuration mode. How long this is must be expressed in milliseconds as a whole, positive integer number, without exceeding 9000 milliseconds.

## Configuring TTL length

Similar to the relay active time, the TTL length parameter cannot exceed 9000 milliseconds and must be expressed in milliseconds as a whole, positive integer number. This parameter is configured in menu item ‘C’ after entering configuration mode and affects both the user-prompted outgoing TTL (‘T’ command) and the ACK TTL, which is sent every time a command is executed.

## Configuring outgoing TTL operating modes

The user-prompted outgoing TTL (‘T’ command) can be configured to operate in two different operating modes, and can also be turned off entirely. Selecting menu item ‘D’ after entering configuration mode will give the user the option to select which operating mode to set.

This TTL is ‘low’ (logical 0) by default, and will only be set to ‘high’ (logical 1) when the ‘T’ command is received, with how it is set varying between operation modes. When high, a non-zero voltage will be observed on the output pin; when ‘low’, a negligible voltage will appear at the output pin.

Below is a short description of each operation mode…

- Toggle is where a TTL is set to high and held at high until the ‘T’ command is called again.
- Pulse is where the TTL is set to high and held only for the amount of time set by the TTL length parameter. When TTL length is elapsed, the TTL will be set back to low.
- Off will simply turn outgoing TTL servicing off, meaning that if the ‘T’ command is received, the microcontroller will only display a message saying that a TTL was requested, but no TTL will be sent.

The outgoing TTL will never be accompanied by an ACK signal, regardless of what operation mode it is operating in.

## Incoming TTL servicing

Servicing incoming TTLs may be useful when synchronising the RECORD system with another external system. By default, external TTL servicing is turned off, but can be turned on via the ‘Y’ command. Upon receiving an external TTL, the Port_3_ISR(void) interrupt service routine (ISR) is called. In version 2.2.0, this ISR does not contain any useful action and must be configured by the user by modifying the firmware; however, actual configuration of the action to be taken when receiving a TTL is a future feature that is under development.

# Calibration and Reconfiguration of Cost Levels for the RECORD System

This guide focuses on the reconfiguration and calibration of LED brightnesses for each feeder at all 3 cost levels. Our RECORD system is able to deliver 3 different levels of cost for our decision-making tasks. This is done through pulse width modulation using crystal oscillator-driven timers on a Texas Instruments MSP430 FR2355 microcontroller.

### Fine-tuned calibration of cost levels in calibration mode

This section covers calibration mode. In this mode, you are able to increase and decrease the CCR value to match a desired Lux value without the need of writing a new value each time. Refer to the LED Calibration document (https://docs.google.com/spreadsheets/u/0/d/1rNoFZjvHOEHzDgk6kuDBNOS2BQlJQwXVIH6rNtAQolY/edit) for information on what Lux you should aim for. You will need a lightmeter on hand to read Lux. DO NOT reconfigure cost levels unless directed and supervised by a lab supervisor. Misconfigurations can and will affect our data!!

1. Follow the steps in the previous section to open a communication channel to the microcontroller.
2. Send a ‘%’ (percent symbol) to enter calibration mode. The microcontroller will respond with instructions on how to proceed.

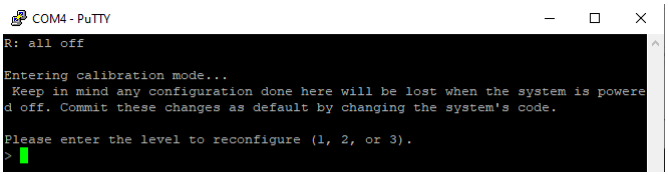
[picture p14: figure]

3. At this point, the microcontroller will ask you for some information, interact with it by using your keyboard. Inputs will automatically be sent without the need to press “Enter” in between inputs. Only one feeder can be calibrated at a specific level at a time.
a. The first prompt will ask you to specify at which level you wish to calibrate a feeder (L1, L2, or L3, see the “What are cost levels?” section for more information). Enter either 1, 2, or 3 only, do not enter letters, a number greater than 3, or less than 1, doing so will result in an error message at a later step.
b. The second prompt will ask you what feeder you wish to calibrate at the specified level. Enter a whole number between 1 and 4, corresponding to each feeder on the arena. Similar to before, do not enter letters, numbers over 4, or numbers below 1:
i. Entering a 1 will reference the feeder at the diagonal zone.
ii. | Entering a 2 will reference the feeder at the grid zone.
iii. | Entering a 3 will reference the feeder at the horizontal zone.
iv. | Entering a 4 will reference the feeder at the radial zone.

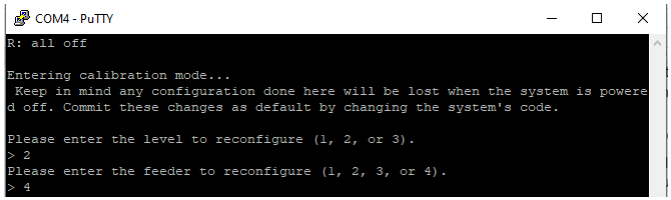
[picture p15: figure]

If an invalid input is entered, an error message will appear and calibration will be aborted. The previously saved parameters will be used until successful reconfiguration.

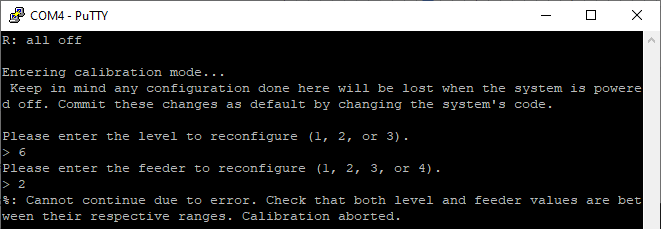
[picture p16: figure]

4. At this point, the feeder you selected should have turned on at the level you’re calibrating. The microcontroller will tell you what CCR value is currently being used for that level, this will be displayed in PuTTY.

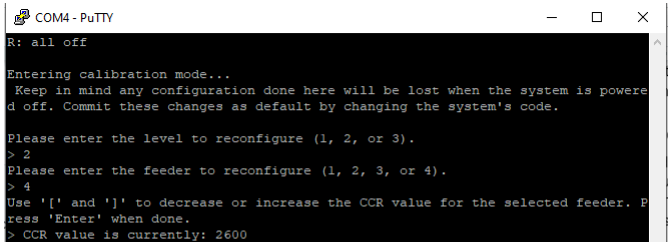
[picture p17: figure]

To increase the brightness on that feeder, one must decrease the CCR value, to do this, use the closing square bracket (‘]’) To decrease the brightness by lowering the CCR value use the opening square bracket (‘[‘). As before, the CCR value will update as you send either symbol, and will be displayed on the PuTTY window.

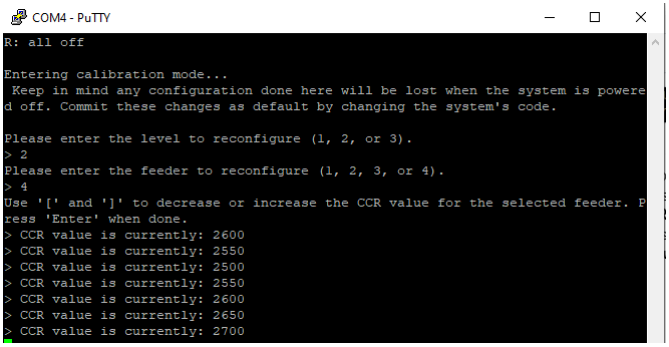
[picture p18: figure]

Measure the Lux at that feeder using the lightmeter and check that the measured value falls within 10 Lux of the target Lux value. Make sure to write this value down along with the CCR value that produced it!
5. Once you are satisfied and have written down both the CCR value and the corresponding Lux value, hit the “Enter” key. The microcontroller will ask you if you wish to save this new CCR value. Enter ‘y’ for yes, and ‘n’ for no.

If you enter ‘y’, the CCR value will be updated and used until the microcontroller is turned off and a message confirming reconfiguration will be displayed and all feeders will be turned on at the level you just calibrated. Only the feeder you were calibrating will be changed, you may be able to tell a difference in brightness.

If you enter ‘n’, all changes from this calibration session will be discarded and the microcontroller will revert back to the last saved CCR value. All feeders will turn on.

6. After the final message is sent, the microcontroller will go back to its idle state and will be able to receive more commands.

Please only calibrate the LEDs under supervision of the PI or a lab supervisor. Small differences in LED brightnesses can affect our data!!

### Reconfiguration of cost levels in configuration mode

This section covers configuration mode. In this mode, you are able to change the CCR value directly to match a desired Lux value. Refer to the LED Calibration document (https://docs.google.com/spreadsheets/u/0/d/1rNoFZjvHOEHzDgk6kuDBNOS2BQlJQwXVIH6rNtAQolY/edit) for information on what Lux you should use. You will need a lightmeter on hand to read Lux. DO NOT reconfigure cost levels unless directed and supervised by a lab supervisor. Misconfigurations can and will affect our data!!

1. Follow the steps in the opening PuTTY section to open a communication channel to the microcontroller.
2. Send a ‘$’ (dollar sign) to enter configuration mode. The microcontroller will respond with instructions on how to proceed.
3. At this point, the microcontroller will ask you for some information, interact with it by using your keyboard. Inputs will automatically be sent without the need to press “Enter” in between inputs. Only one feeder can be calibrated at a specific level at a time.
a. The first prompt will ask you to specify at which level you wish to calibrate a feeder (L1, L2, or L3, see the “What are cost levels?” section for more information). Enter either 1, 2, or 3 only, do not enter letters, a number greater than 3, or less than 1, doing so will result in an error message at a later step.
b. The second prompt will ask you what feeder you wish to calibrate at the specified level. Enter a whole number between 1 and 4, corresponding to each feeder on the arena. Similar to before, do not enter letters, numbers over 4, or numbers below 1:
i. Entering a 1 will reference the feeder at the diagonal zone.
ii. | Entering a 2 will reference the feeder at the grid zone.
iii. | Entering a 3 will reference the feeder at the horizontal zone.
iv. | Entering a 4 will reference the feeder at the radial zone.

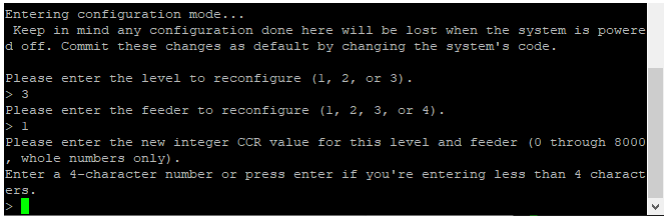
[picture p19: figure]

4. The microcontroller will ask for a new CCR value for the level and feeder you are reconfiguring. Enter a whole number between 0 and 8000 only. If your new CCR value consists of three digits or less, press the “Enter” key to submit the new value.

Please refer to the LED Calibration (https://docs.google.com/spreadsheets/u/0/d/1rNoFZjvHOEHzDgk6kuDBNOS2BQlJQwXVIH6rNtAQolY/edit) spreadsheet for information about what values result in what Lux. Only use values contained in this spreadsheet unless you are calibrating a feeder!

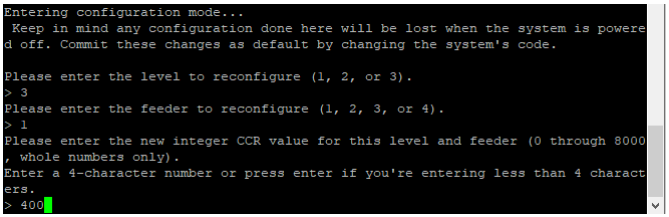
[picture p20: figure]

5. After entering four digits or pressing the “Enter” key, the microcontroller will ask you if you would like to preview the new brightness. Enter ‘y’ for yes, and ‘n’ for no.

If you enter ‘y’, all feeders will turn on at the level you have just reconfigured, however only the feeder you specified in step 3 will be affected. Changes will be applied and saved for the rest of the session (until the microcontroller is turned off).

If you enter an ‘n’, the new CCR value will still be applied, but the feeder will need to be turned off and then back on again for the changes to become evident.

If an invalid input is entered, an error message after the new CCR value is entered will appear and calibration will be aborted. The previously saved parameters will be used until successful reconfiguration.

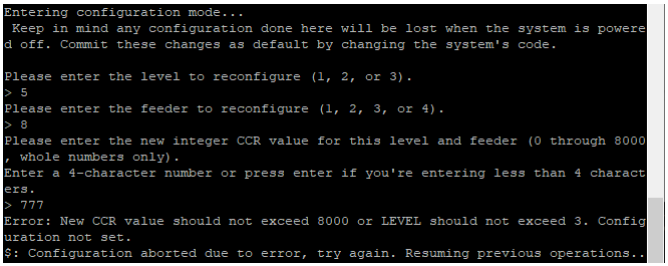
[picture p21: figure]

6. Measure the brightness of the feeder using a lightmeter, then record the new CCR value and its corresponding Lux value. After the final message is sent, the microcontroller will go back to its idle state and will be able to receive more commands.

Please only calibrate the LEDs under supervision of the PI or a lab supervisor. Small differences in LED brightnesses can affect our data!!

## Suggested procedure to calibrate LEDs

### Relevant documentation

Refer to the following documentation when calibrating the RECORD system feeder LEDs:
1. LED Calibration Data: (https://docs.google.com/spreadsheets/u/0/d/1rNoFZjvHOEHzDgk6kuDBNOS2BQlJQwXVIH6rNtAQolY/edit)
a. Arena 1 Calibration (Sheet)
b. Arena 2 Calibration (Sheet)
c. Arena 3 Calibration (Sheet)
d. Arena 4 Calibration (Sheet)
e. Per-Rat Lux Requirements (Sheet)
2. Reconfiguration of cost levels in configuration mode
3. Fine-tuned calibration of cost levels in calibration mode

Note: DO NOT edit these documents unless otherwise instructed to by the PI or a lab supervisor!

### Creating LED lines of best fit to aid in calibration

The “calibration lines” or “trend lines”, help us estimate a CCR value that may possibly produce the appropriate amount of Lux we are looking for. These are calculated from “calibration curves”, which we create by measuring Lux at 6 different CCR values. The calibration line is the trend these curves follow, also known as the “line of best fit” or “regression line”, which results from a statistical calculation called the “Least Square Method”. Our LED Calibration Data (https://docs.google.com/spreadsheets/u/0/d/1rNoFZjvHOEHzDgk6kuDBNOS2BQlJQwXVIH6rNtAQolY/edit) document does this automatically, all that needs to be done is enter the 6 measurements mentioned before. The following steps will guide you on how to do this, you will need a lightmeter able to measure up to 1000 Lux to proceed.

1. Open the LED Calibration Data (https://docs.google.com/spreadsheets/u/0/d/1rNoFZjvHOEHzDgk6kuDBNOS2BQlJQwXVIH6rNtAQolY/edit) document and open one of the Arena Calibration sheets. You will be met with a small table with numbers, underneath it will be a large graph with four coloured lines, these are the calibration curves.
2. Check with a lab supervisor or the PI to know if the data is accurate; the date of last measurement is located to the right of the first table on cell H2, the data may or may not need to be updated, depending on changes made to the arenas. If an update is needed, proceed to step 3.

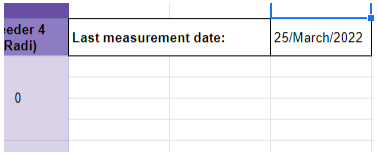
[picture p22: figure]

3. Open PuTTY and connect to the microcontroller for the arena you are calibrating, see the “Opening PuTTY and connecting to an arena microcontroller” section on this guide for instructions on how to do so.
4. Using the steps in the “Reconfiguration of cost levels in configuration mode” to enter configuration mode on the microcontroller, start by configuring the microcontroller to turn all the feeders on to a CCR value of either 6400, 4800, 3200, 1600, or 1. You may choose any level for this calibration when prompted.
5. Turn on the lightmeter and make sure to set it to measure Lux, not Fc or Lumen. Then, set the measurement range to 0 - 2000 Lux by pressing the “R” button until the range indicator on the bottom on the lightmeter screen underlines the 2000 Lux range, you may be able to measure using the lowest range if you are calibrating cost level 1, but if the lightmeter reads “OL” at any point, you will need to step up a range. Finally,
because the measured value will constantly be changing, it helps to take only the maximum value. Point the light sensor (it looks like a white half-sphere) and set the lightmeter to “Max” mode then at a dark spot on the arena, this will freeze the measured value.
6. Start by measuring feeder 1 on the horizontal corner of the arena. Take the light sensor and hold it about 3 millimetres or less above each one of the four LEDs on the feeder, holding it in place for 2 to 3 seconds. The lightmeter will display the maximum value it was able to measure. It is recommended you measure each feeder at least twice, as there will be a wide variability in the measurement.
7. Record the values you measured for each feeder into the appropriate row for the CCR value you’re measuring, you’ll start to see the calibration curve graph change.
8. Once you are done with that CCR value, move on to the next and repeat steps 4 through 7 until you’ve measured all feeders at each CCR value.
9. The trend line equation will appear on the calibration curve graph in the legend on the right side.

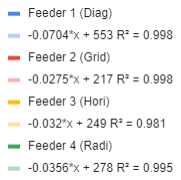
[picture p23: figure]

X in this equation is the CCR value, and Y is the Lux. R

2
is the correlation coefficient, the higher this number is, the better the line fits the data, you do not need to worry about this value for now. Let’s generalise this equation to Y = Afdr*X + Bfdr, where Afdr and Bfdr are the corresponding slope and Y-intercept values for each feeder’s trend line. This is the first and last bit of maths you’ll need to know for this guide.
10. Solve the equations for X. Below is an example using the first equation marked in muted blue:

Y = -0.0704 X + 553
Y - 553 = -0.0704 X + 553 - 553
Y - 553 / (-0.0704) = (-0.0704 X) / -0.0704 Y - 553 / (-0.0704) = X
Set up this equation in terms of spreadsheet cells for the CCR value estimator:
a. For feeder 1, enter “=ROUND((R33-Bfdr)/Afdr)” into cell R34
b. For feeder 2, enter “=ROUND((R36-Bfdr)/Afdr)” into cell R37
c. For feeder 3, enter “=ROUND((R39-Bfdr)/Afdr)” into cell R40
d. For feeder 4, enter “=ROUND((R42-Bfdr)/Afdr)” into cell R43
11. Once done setting up the CCR value estimator, you are done. Notify a lab member to double check your work!

### Calibrating feeder LEDs to rat-specific required Lux values

It is important to know where to start with the calibration process. We have set up a chart with target lux values, individualised for each rat in the Per-Rat Lux Requirements sheet on the LED Calibration Data (https://docs.google.com/spreadsheets/u/0/d/1rNoFZjvHOEHzDgk6kuDBNOS2BQlJQwXVIH6rNtAQolY/edit) documentation. This document tells you what Lux value to aim for at each cost level when calibrating the RECORD system; but how do you know what CCR value will give you these values?

In the same document, there are four sheets that describe the LED brightness behaviour at each arena, we call these “calibration lines” or “trend lines”. These graphs are carefully created by our team to predict a ballpark estimate of the CCR value needed for the desired Lux values. The sheets also contain a history of CCR values that were found to produce a Lux value within the desired ranges, in case we need to dial back or crank up the brightness without putting in more effort than needed. See the “Creating LED calibration lines to aid in calibration” section in this guide to learn how these calibration lines are obtained.

Follow the following steps to begin calibrating, you will need a lightmeter able to measure up to 1000 Lux to proceed:

1. Open the Per-Rat Lux Requirements sheet (https://docs.google.com/spreadsheets/u/0/d/1rNoFZjvHOEHzDgk6kuDBNOS2BQlJQwXVIH6rNtAQolY/edit) and refer to columns E, F, and G to find out what Lux value you are to aim for. Choose a level, then choose a Lux value to begin with, this will be your target Lux value.

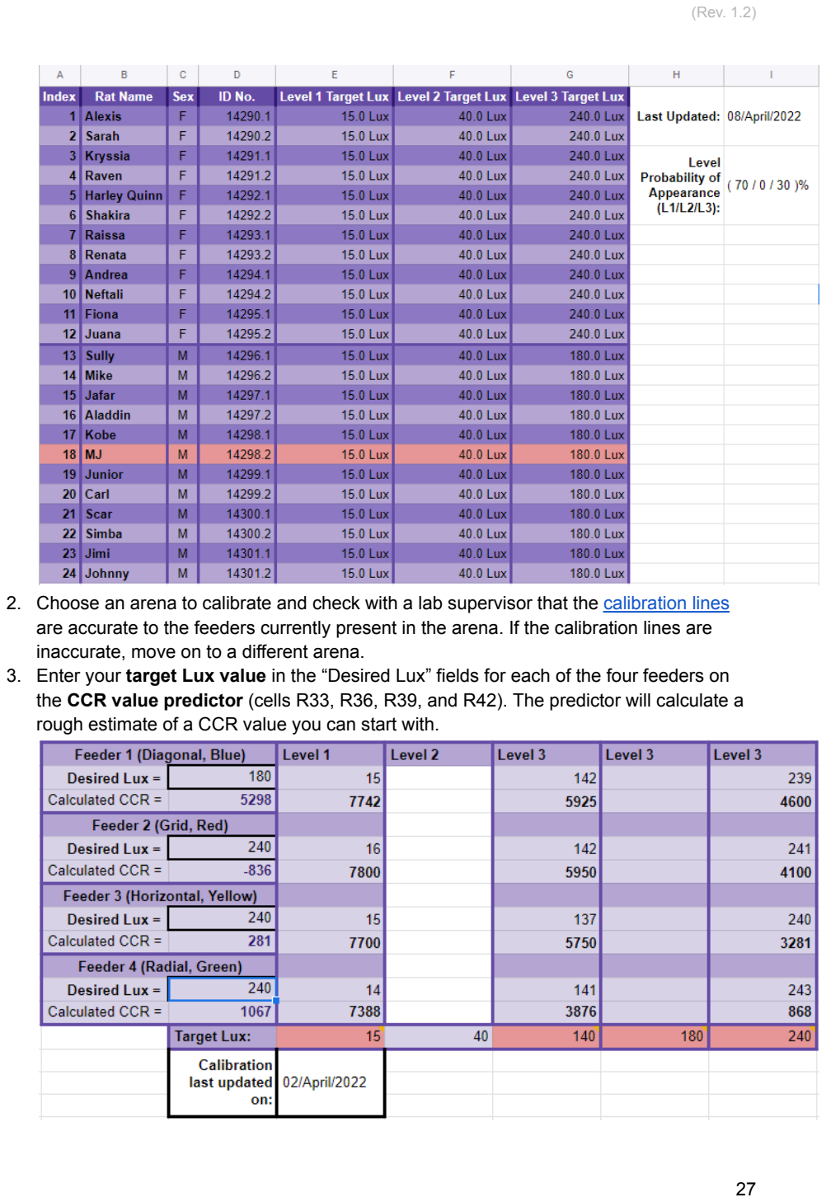
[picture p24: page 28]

2. Choose an arena to calibrate and check with a lab supervisor that the calibration lines (https://docs.google.com/spreadsheets/u/0/d/1rNoFZjvHOEHzDgk6kuDBNOS2BQlJQwXVIH6rNtAQolY/edit) are accurate to the feeders currently present in the arena. If the calibration lines are inaccurate, move on to a different arena.
3. Enter your target Lux value in the “Desired Lux” fields for each of the four feeders on the CCR value predictor (cells R33, R36, R39, and R42). The predictor will calculate a rough estimate of a CCR value you can start with.

Note: If the calculated CCR value happens to be negative, continue with a value of 0. If it is over 8000, proceed with a value of 8000. Do not use any values lower than 0, or above 8000, as this may result in unexpected microcontroller behaviour.
4. Open PuTTY and connect to the microcontroller for the arena you are calibrating, see the “Opening PuTTY and connecting to an arena microcontroller” section on this guide for instructions on how to do so.
5. With the estimated CCR values you got, enter configuration mode on the microcontroller by sending a dollar sign (‘$’) to the microcontroller.
6. Follow the steps in the “Reconfiguration of cost levels in configuration mode” to enter the estimated CCR values to the microcontroller. You may or may not be able to see the lights change in brightness. Don’t worry if you can’t, we’re making very small changes to the brightness here.
7. Turn on the lightmeter and make sure to set it to measure Lux, not Fc or Lumen. Then, set the measurement range to 0 - 2000 Lux by pressing the “R” button until the range indicator on the bottom on the lightmeter screen underlines the 2000 Lux range, you may be able to measure using the lowest range if you are calibrating cost level 1, but if the lightmeter reads “OL” at any point, you will need to step up a range. Finally,
because the measured value will constantly be changing, it helps to take only the maximum value. Point the light sensor (it looks like a white half-sphere) and set the lightmeter to “Max” mode then at a dark spot on the arena, this will freeze the measured value.
8. Start by measuring feeder 1 on the horizontal corner of the arena. Take the light sensor and hold it about 3 millimetres or less above each one of the four LEDs on the feeder, holding it in place for 2 to 3 seconds. The lightmeter will display the maximum value it was able to measure. It is recommended you measure each feeder at least twice, as there will be a wide variability in the measurement.
a. If the value you measured is within ±10 Lux of the target Lux, record this value, the CCR value that produced it, and which feeder on which maze you were calibrating.
b. If the value is not within ±10 Lux of the target Lux, use calibration mode on the microcontroller by sending a percent sign (‘%’) to finetune the CCR value and repeat steps 7 and 8 until you reach the target. For instructions on how to operate in calibration mode, see the Fine-tuned calibration of cost levels in calibration mode section in this guide. Once you have reached your target, save the new CCR value, and record it like you would in (a).
9. Move on to the next feeder. Once you are done, double check your data and hand it to a lab supervisor so that they may database it.

# How to upload/update Firmware on a Texas Instrument Microcontroller Dev. Board

This guide assumes the user has an existing workspace and project for their microcontroller development board and is specific to Texas Instrument products. Please ensure you are using a Texas Instruments microcontroller development board.

Before starting, disconnect all microcontrollers from the PC and leave only the one to be updated connected. Make sure the microcontroller is on and functioning correctly by looking for a green light on the top of the microcontroller. If everything looks fine, proceed.

1. Start by opening Code Composer Studio. The software version shown in this guide is Version: 10.2.0.00009.
2. Drop down your project hierarchy on the Project Explorer panel on the left side of the screen.

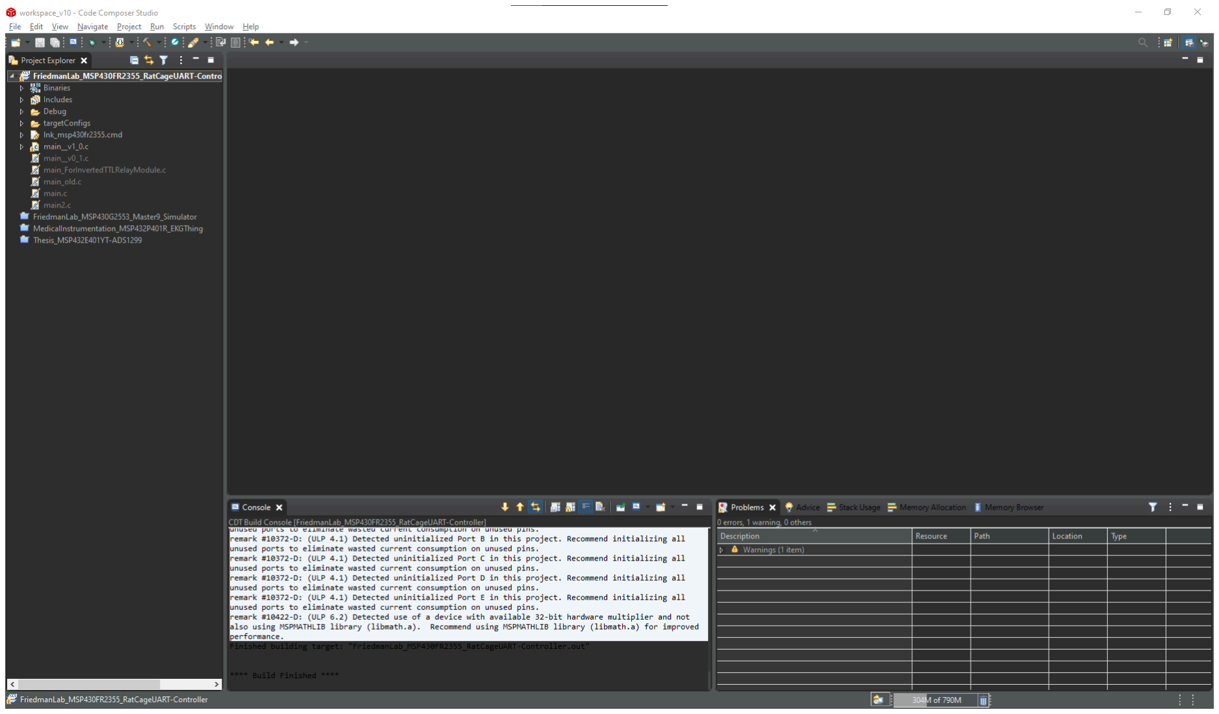
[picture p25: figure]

3. Right-click on the top of the hierarchy, then navigate to “Show in Local Terminal”. Click on “System Explorer” to open the folder where your entire workspace is saved.

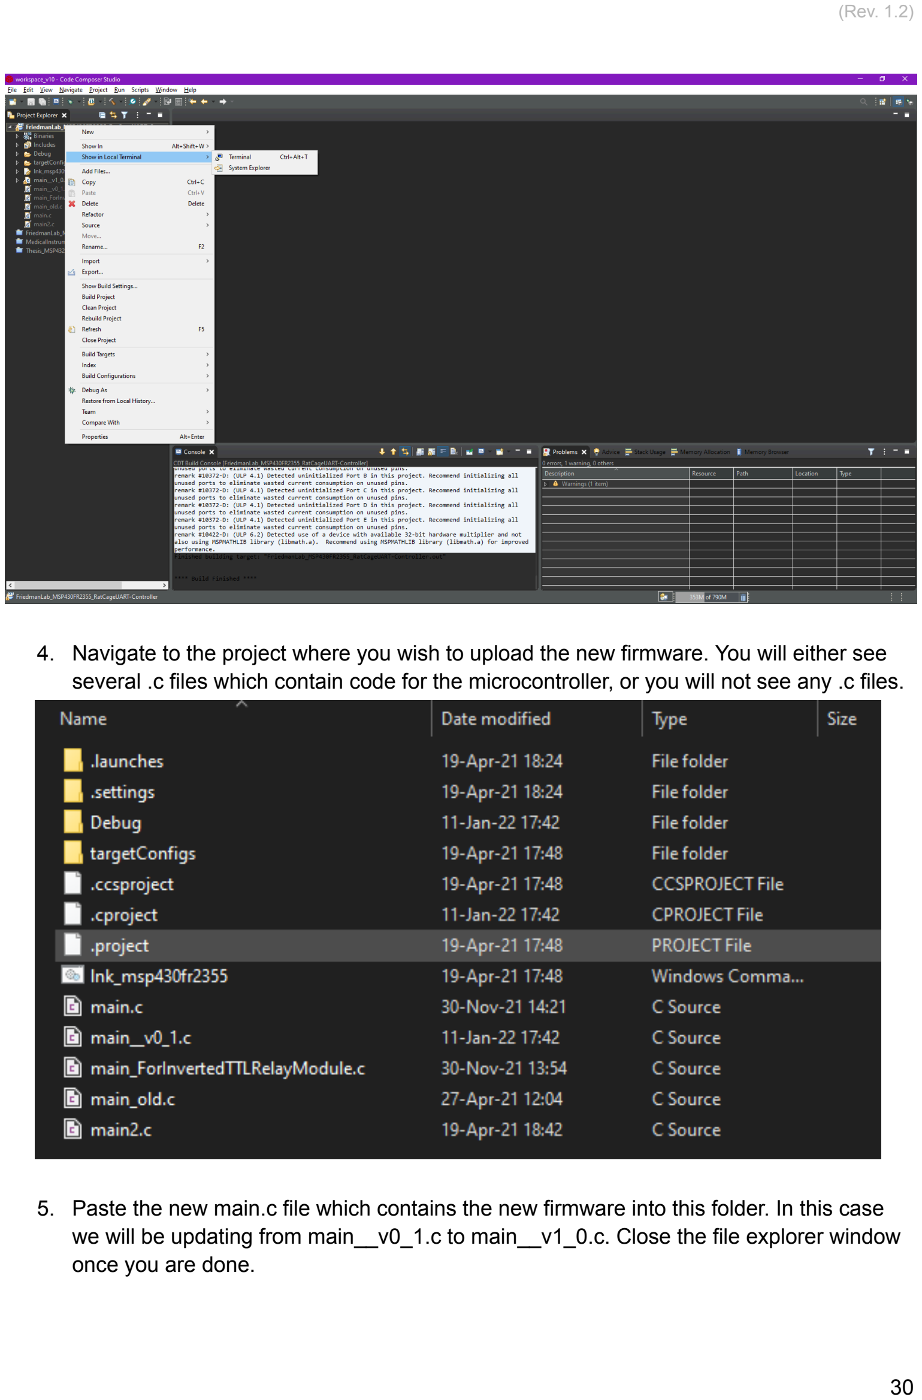
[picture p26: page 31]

4. Navigate to the project where you wish to upload the new firmware. You will either see several .c files which contain code for the microcontroller, or you will not see any .c files.
5. Paste the new main.c file which contains the new firmware into this folder. In this case we will be updating from main__v0_1.c to main__v1_0.c. Close the file explorer window once you are done.

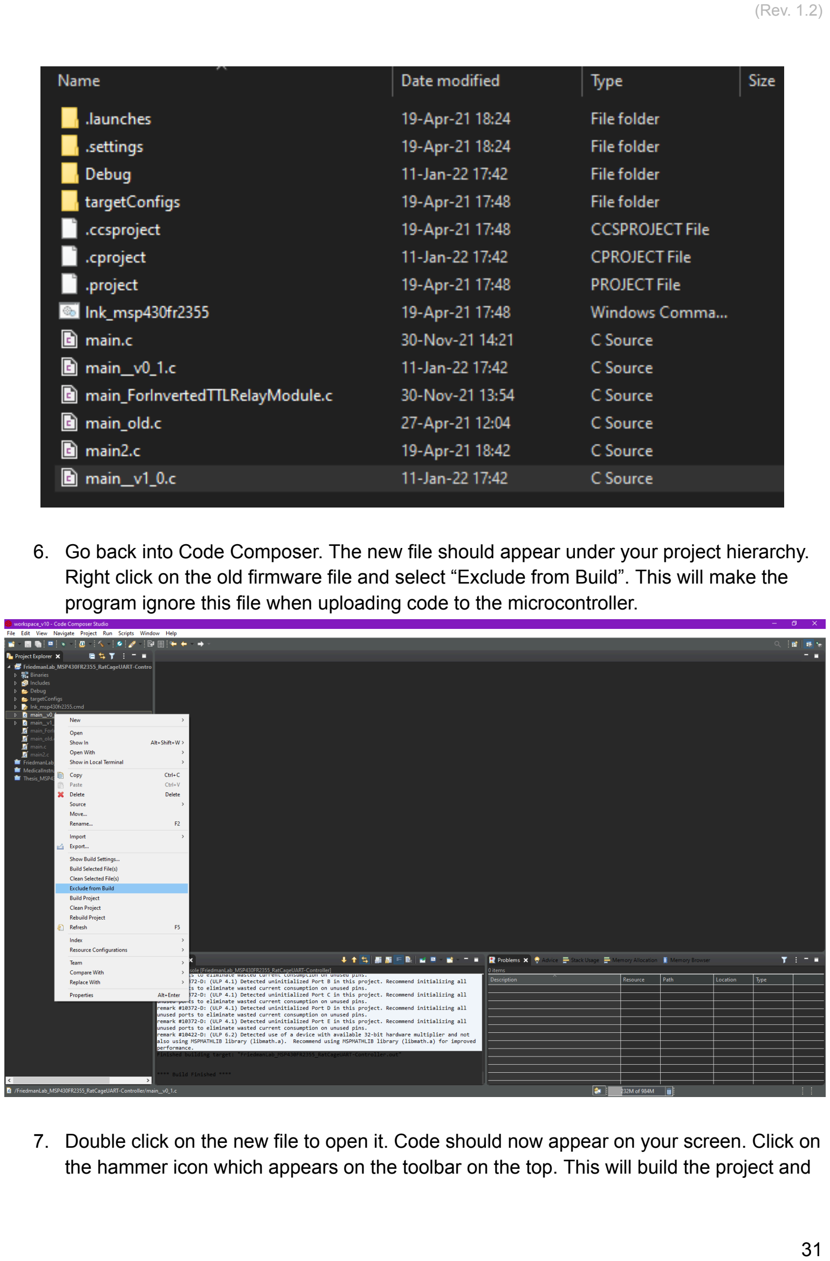
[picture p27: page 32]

6. Go back into Code Composer. The new file should appear under your project hierarchy. Right click on the old firmware file and select “Exclude from Build”. This will make the program ignore this file when uploading code to the microcontroller.
7. Double click on the new file to open it. Code should now appear on your screen. Click on the hammer icon which appears on the toolbar on the top. This will build the project and check the new code for errors. Text will appear on the console located on the bottom of the screen, simply wait for it to finish. The first build may take longer than subsequent ones.

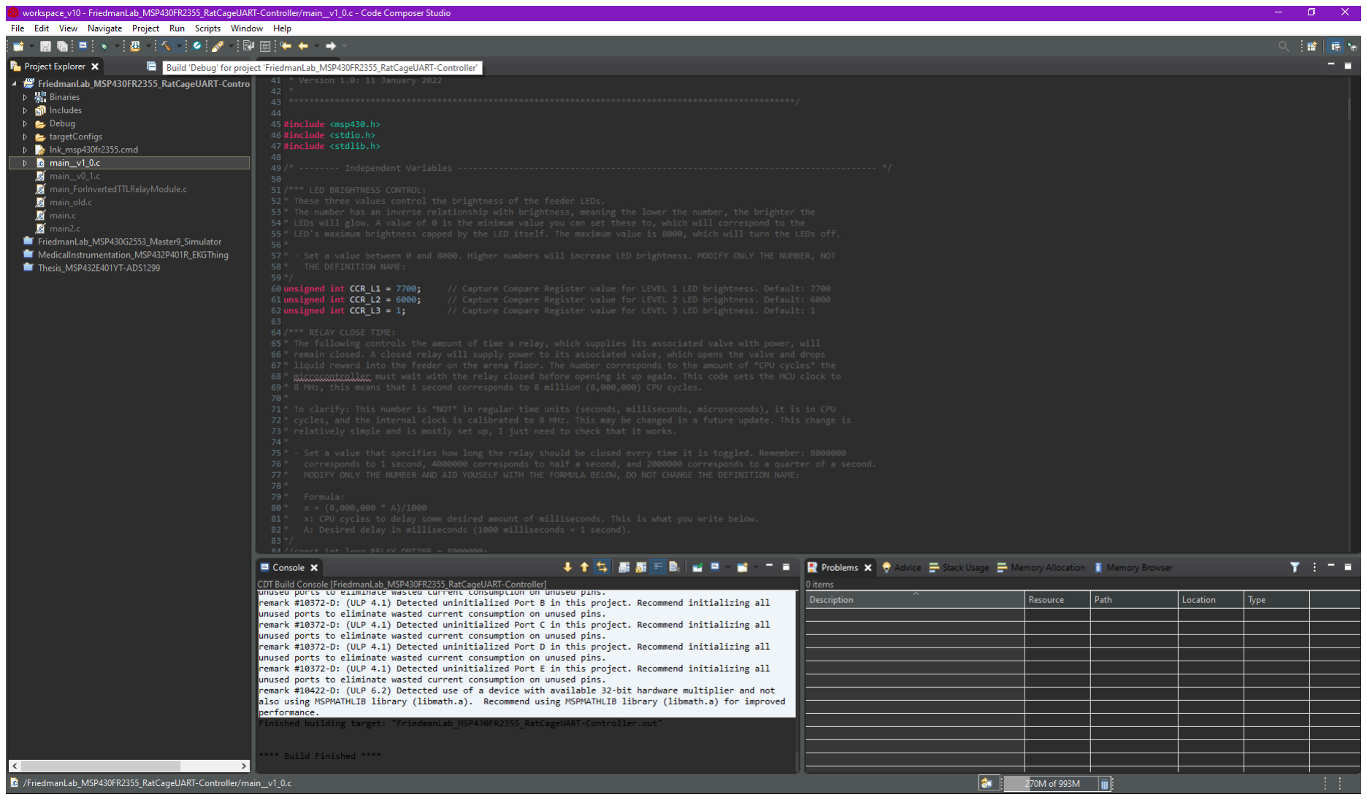
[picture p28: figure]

8. Click on the Flash icon located to the left of the hammer icon. This will upload the code to the microcontroller. Click okay if the program asks you to Save and Launch and then click Proceed on the next prompt.

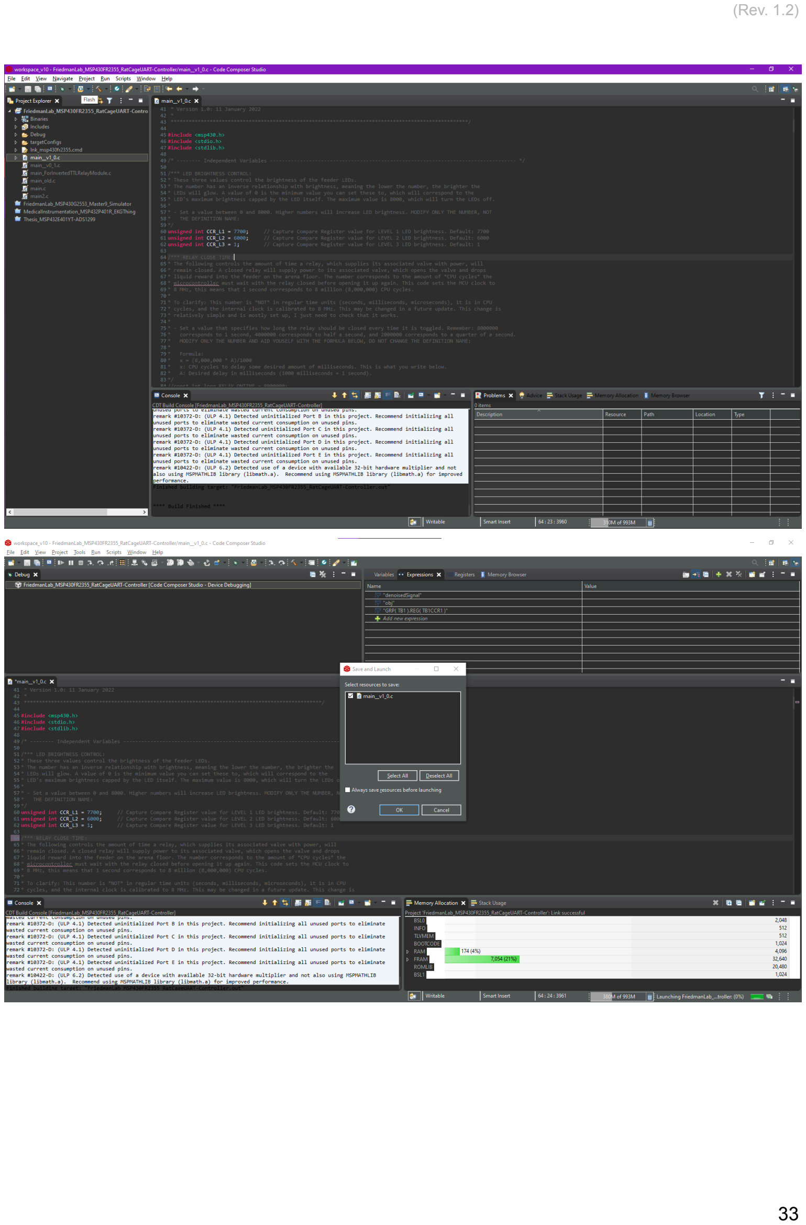
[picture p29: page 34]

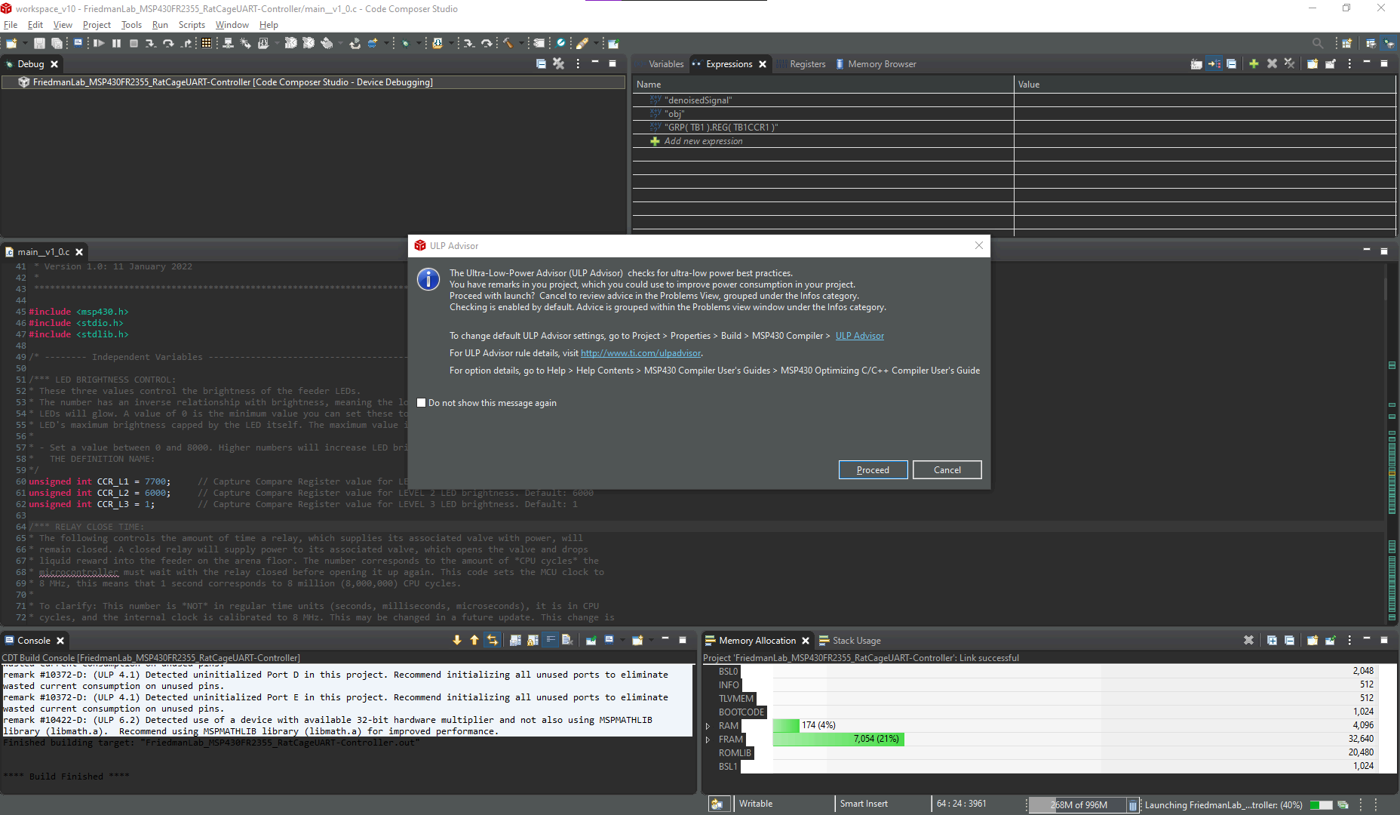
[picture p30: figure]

9. The code has now been uploaded to the microcontroller. You may begin using it immediately.

Sometimes, new firmware may be buggy and one may need to roll back an update. To do this, repeat step 6 to re-include the old firmware code in the build, and instead exclude the new firmware code from the build. Then continue on to the next steps.

# A note about RECORD and Noldus Ethovision

RECORD is a behavioural setup that is compatible with various animal tracking solutions, one example of this is Noldus’ Ethovision XT. We have set up various experiments using this software which can be found in the RECORD github repository (https://github.com/rjibanezalcala/RECORD/tree/main/ethovision_experiments). In order for RECORD to function with Ethovision, the experiment’s trial control must access batch scripts to send the appropriate commands to the arena microcontrollers and execute “trial events”. Afterwards, the computer must wait for the MCU to finish executing a command and re-synchronise. Because of this, trial events tend to have some “overhead” and “tail”.

We define “overhead” as the time it takes to access a batch script to execute it. The delay is determined by batch file access time and execution time. This time is typically negligible for a single event, but once several events are executed, it can add a small amount of delay to a trial, especially if the file access time on the computer is substantial. Additionally, the batch files introduce a second delay between sending commands to the different arenas. This is because one instance of Plink must be created to send commands to each arena. This delay may be tweaked on the “timeout” function in the batch files, however, it is not recommended to reduce this too much if all MCUs are sharing the same data bus, or are connected to the same USB port.

The “tail” is defined as the time it takes to execute the command, and re-synchronise devices post-execution. This is defined as command execution time on the MCU, plus trial control delays and re-synchronisation. This will likely introduce the largest delays in the trial, extending trial time. Different commands will take different times to execute on the MCU, most of the time, the commands that take the longest will be any commands that open the solenoid valves due to the delay needed to keep the valve open so that enough reward is dispensed as well as the TTL pulse that is sent after command execution. These delays can be tweaked on each MCU setup file and flashed in Code Composer (see How to upload/update Firmware on a Texas Instrument Microcontroller Dev. Board), or can be temporarily changed in configuration mode (see Configuring relay active time and Configuring TTL length). The tail time also includes re-synchronisation trial control delays. Without these delays, the computer and MCU might start running out of sync, and trial events will not be executed. The computer must then wait for an acknowledgement signal from the MCU each time a command is sent using a system delay, some hardware polling (on the I/O box), and finally an additional delay to allow the MCU to return to its baseline state. For more information on how these delays are handled, please see the figure included in this section.

## The inter-trial interval (ITI)

While the ITI can be programmed on Ethovision in the “Acquisition” screen, the time a rodent waits in-between trials consists of a trial setup period, a trial cleanup period, and the
programmed ITI (see figure below). This amounts to approximately 28 seconds if no tweaking is made to the original RECORD source files.

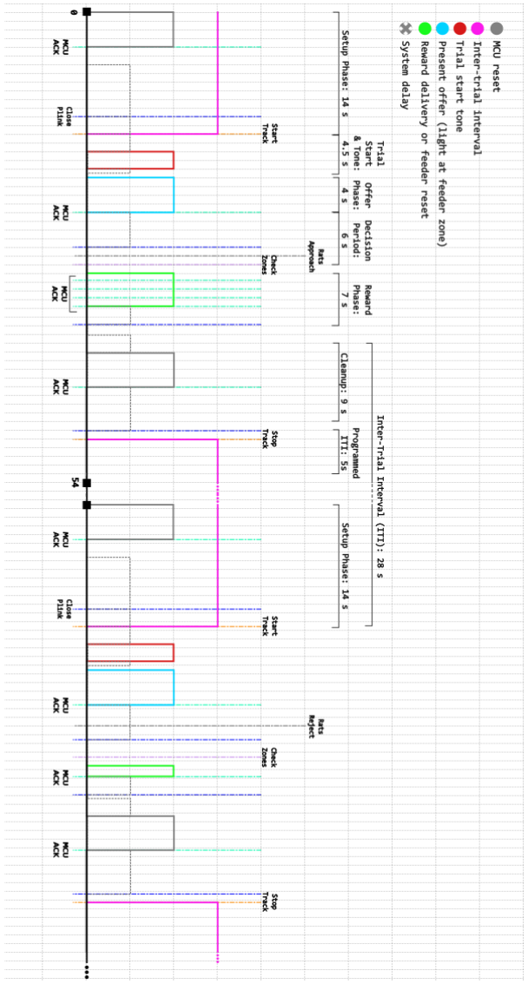
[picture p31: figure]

# Troubleshooting

By Graham Waller and Raquel Ibáñez Alcalá

__________________________________________________________________________

## Hardware troubleshooting

Anything concerning the physical components of the RECORD electronics and arenas will be contained here. When in doubt, turn everything off and on → unplug and plug. Make sure everything, from the wires and cables, to the tubes that deliver sucrose, is connected.

### Valves and Relays

Problem: Relay clicking, but valves not clicking…
Solutions: Before proceeding, check that the valve cable is connected to a valve on one side, and to the corresponding slot on the RECORD box or circuit board on the other side.Use PuTTY to activate each valve individually by sending “F” for valve 1, “G” for 2, “H” for 3, then “J” for 4, and identify which valve clicks and which does not. See Protocol for using PuTTY on slack in #important-documents.

If you have at least one valve that does click, swap the connectors for a working valve and a non-working valve then use PuTTY to activate both valves.
a. If the non-working valve clicks and the working valve does not, the problem may be at the valve cable. Proceed to step (1) below.
b. If the working valve clicks and the non-working valve does not, the valves may be the problem. Jump to step (3) below.

If no valves click, make sure that the valves are being supplied the correct voltage for them to operate (15 V - 24 V). Check that the power supply cable is connected to the RECORD box and the valve power supply is turned on, then test again. If the problem persists, proceed to step (1) below.

1. Check connections and cables for short circuits. Make sure all exposed copper wire is shielded; wires should not be touching neighbouring wires at the head of connections to the PCB or the valves. If needed, tape each individual section of exposed wire with electrical tape to shield connections from one another.
2. Check the connector at the valve side of the valve cable, it is possible that the wire may have come loose from its housing and might not be making contact with the connector on the valve. Alternatively, the contacts on the connectors may be dirty. Disconnect the valve from the cable and clean the contacts using a damp paper towel, then connect them again.

3. If the problem persists, it may be necessary to either clean or replace the non-working valve(s). To clean the valve, dismount it from the valve stand, remove the solenoid from it, and submerge the valve plunger in water for at least 1 hour, then test it again.

Problem: Relays not clicking…
Solution: Likely caused by a connection issue between the microcontroller and relays. Carefully open the RECORD box and look for the wires that connect the microcontroller (in red) and the relays (long blue board featuring several blue blocks with white writing). If these wires are disconnected, the relays will not click. Refer to the Electronics build guide to repair and ask a lab supervisor for help, do not connect or disconnect anything on the PCB or microcontroller without supervision.

Problem: Valves and relays are clicking, but no sucrose is being dispensed…
Solution: This is likely caused by air being trapped in the system. Before proceeding, check that all tubing is connected to its corresponding feeders. Check for air bubbles in the tubing between the syringes and the valves, and between the valves and the arena feeders. If there are bubbles present, activate the valves a few times using PuTTY, or run the system_cleanup batch script routine. You may also force sucrose solution into the system by using the syringe plunger to push down the solution while the valves are open. To do this, take a syringe plunger and while activating the valve with PuTTY, push the plunger down the syringe to flush liquid through and clear the blockage. When finished, check for leaks in the system and fix them accordingly.
_______________________________________

### Lights

Problem: Light does not turn on for one or more feeders...
Solutions:
1. Make sure that the feeder lights are active at any (visible) brightness. Use PuTTY to turn the lights on. See Protocol for using PuTTY on slack in #important-documents.
2. Check that the non-working feeder lights are connected to the LED cable, this should be a two-wire connector that attaches to the cable. If the feeder is connected, make sure the lights are not connected backwards. Some feeders will have a blue and black wire pair, others will have a yellow and green wire pair, and (though uncommon) others may have a red and black wire pair. Make sure that the black wire on the LED cable (representing ground) is connected either to the black or green wire on the feeder LEDs, and the red wire on the LED cable (representing live wire) is connected to the yellow, red, or blue wire on the feeder LEDs. The light should turn on after this.
3. If the light does not turn on, or if one some LEDs turn on on that feeder, lift the feeder up by pushing the “tail” of the feeder up (where the tubing attaches) and pull it up and off the feeder base. Flip the feeder over and look at the underside. Carefully separate any exposed metal contacts on the LED ring bundle, making sure there are no short-circuits in the loop. Handle these wires with care, making sure not to break any of the connections. The lights should turn on after separating all the wires.

4. If the lights still do not turn on, check connections and cables for short circuits. Make sure all exposed copper wire is shielded; wires should not be touching neighbouring wires at the head of connections to the PCB or the valves. If needed, tape each individual section of exposed wire with electrical tape to shield connections from one another.

Problem: Two lights turning on at once…
Solution: The given cable’s copper wires are likely touching at the white connector on the end of the cable which connects to the RECORD box. Use electrical tape to shield each individual exposed copper wire to prevent the wires from touching one another.

_______________________________________

### Arena Pieces

Pieces will wear down and come apart over time, this process can happen a lot sooner if the rats gnaw on the arena. Simply replace faulty pieces with new parts and/or glue them back together.

__________________________________________________________________________

## Ethovision troubleshooting

Good rule of thumb to avoid issues in EthoVision is to set the program priority for EthoVision to “Real Time” via TaskManager (ctrl → shift → esc) and having other programs (especially big ones like MatLab and Google Chrome) closed while running trials.

Problem: Trials getting stuck at the beginning stage...
Alternative problem 1: Trial never ends…
Alternative problem 2: Lights stay on after a trial ends…
Solution: Caused by desynchronization between the RECORD system and the animal tracking software. Stop the trials. Close all command windows that may have been left open, then turn the microcontrollers off, wait up to 10 seconds, and turn them back on. Do this only after stopping the trials, doing so during a trial will desynchronize both systems again!

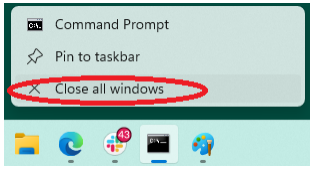
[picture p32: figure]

If the problem persists, check that the microcontroller is connected to the I/O interface via one of the data lines on the hardware synchronisation cable. It is possible that the connection might need to be flipped around so that the output from the microcontroller goes to the TTL input line, and the input for the microcontroller goes to the TTL output line.

Changes to the trial control may be needed if the problem persists as the trial may not be allowing enough time for the microcontroller to resynchronize with the trial after running a command, or the serial communication channel may be closing prematurely.

Problem: EthoVision crashed and data was not recovered…
Solution: This is more of a workaround than a solution. Create a backup of the experiment, then create a new experiment and delete any other behavioural task trial control structures from the one which you wish to run. A good practice is to keep different task versions in separate experiments, and always back up your experiments. This is to keep bugs in the program isolated to only one experiment.

Problem: A feeder has a significant delay before delivering sucrose in one or more arenas… Solution: Check configuration for zones under the trial control settings, make sure that options for each decision-making condition variable (box x accepts, box y rejects, etc.) are set to the appropriate settings. Also increase the time for which accept/reject conditions must be met (for example 0.5s might be too low, and should be increased to 1.0s).
Example: We incurred this error when the condition check in “box 4 rejects” was set to “when centre-point is in all zones simultaneously” instead of “in any of the zones” in the trial control settings. This made the trial hang because that condition can never be met as the rat cannot exist in more than one zone simultaneously, and the program was waiting until the “box 4 accepts” condition was met.

Problem: The Windows “USB disconnect” sound plays when more than one valve/relay clicks, then the current trial never ends…
Solution: This may be due to a power supply overload in the system, which makes the microcontrollers reset and de-synchronizes them from EthoVision.

If this happens to you in the middle of running trials, manually stop the trial, close all command windows, and continue running trials.

To prevent this problem from happening again, modify the trial control in EthoVision so that the delivery stage at each arena is delayed 0.5 seconds after the previous one, this will ensure that valves don’t click at the same time and that the power supply for the relays is not overloaded.

Problem: Ethovision gives an error saying calibration lines are significantly different, when editing arena settings…
Solution: A new calibration line that is significantly smaller or bigger than the others may have been accidentally added. This causes a conflict between the existing calibration lines which measure the arenas at 64.5cm. To solve, delete the new calibration line that was accidentally created.

Problem: RECORD hangs at the reward delivery stage of the trial…
Solution: Sometimes during a trial, the RECORD system will hang at any stage of the trial, especially the reward delivery. This is normal. Reward delivery is heavily dependent on animal detection and this may sometimes cause delays depending on the animal’s position. If the system does not respond after 10 - 20 seconds, manually stop the trial and troubleshoot the detection settings or arena settings. Make sure to close all command windows (small black windows) before starting the next trial. This will ensure that the RECORD system will be responsive for the next trial.

__________________________________________________________________________

## Firmware troubleshooting

It is rare for the firmware running on the microcontroller to act up. Firmware is debugged before uploading it to the microcontroller. Fixes to the firmware will require C language programming skills, but a good solution that will work most of the time is to turn the microcontroller(s) off, wait 10 seconds, then turn it back on.

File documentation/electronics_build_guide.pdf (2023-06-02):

Written by Raquel Ibáñez Alcalá, Graham Waller, Monica Ponce, Neftali Reyes, Karen Arzola, Safa Hosain, and Andrea Macias Created 30/May/2023, last updated 2/Jun/2023 (Rev. 1.1)

R.E.C.O.R.D.

(Reward-Cost in Rodent Decision-making)

# Electronics build guide

Revision 1.1

(Rev. 1.1)

## Table of Contents

# Overview

This assembly guide will instruct you in your creation of the electronic components of our custom arena behavioural apparatus. These components are made utilising basic wires, lights, and cables, to allow for a taylormade task to be used in the study of decision-making and disorders in rodents in a cost-effective and open-science friendly way. The customization of our system allows for on the fly changes and adaptations to the experimental environment and process, as well as animal behaviour. Further, it enables the interchangeability and replacement of parts as they wear down over the course of thousands of behavioural trials. In this guide you will find the parts and materials, dimensions and measurements, along with links and assembly instructions, to our custom electronic system as well as the code and programs that we are using to manipulate it.

# LED assemblies and cable

CAUTION: You will be working with very hot equipment in this section. Please make sure you take the proper precautions to not burn yourself, other team members, or any objects inside and outside of your work area!

The LED assemblies on the arena signal a cost (associated with the food rewards) at each corner. Eacha arena will house four of these assemblies, mounted onto every feeder piece in the arena. Each assembly is made up of four LEDs connected in parallel and are controlled by a single data wire, with a single ground wire providing them ground. By the end of this section you should have 4 LED modules, each made up of 4 LEDs, with one red wire and one black wire coming out of the assembly.

## Materials

- 16 blue LEDs
- Black wire
- Red wire
- Dupont wire, female, red
- Dupont wire, female, black
- Two-conductor speaker wire
- Electrical tape
- soldering iron
- Solder
- Wire strippers
- Wire cutters
- Multimeter

### 1. LED Anatomy

Every LED has two “legs”; one receives voltage from a source and the other completes the circuit by allowing the current to flow towards ground. These are called “anode” and “cathode”, respectively. The anode and cathode can be identified by observing the LED legs, the anode is the longer leg while the cathode is the shorter leg, see Figure 2.1 for reference.

Figure 2.1. Identifying the cathode and anode:

Figure 2.1 A: Illustration showcasing the anode vs cathode based length leg size.

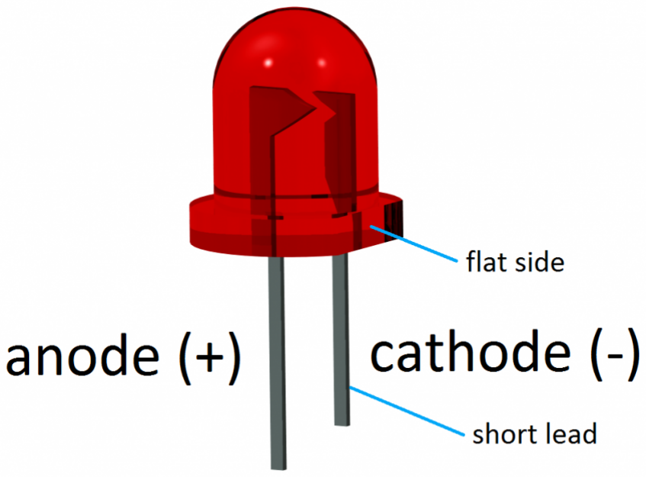
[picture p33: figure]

### 2. Preparing the Wires

Using the wire cutters, measure and cut three 4 cm segments of both red and black wire. Strip both ends of all wire segments using wire strippers, being careful not to cut the wire (or yourself) by accident.

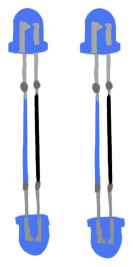
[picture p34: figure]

### 3. Soldering Preparation

Make sure the soldering iron is resting in its holder and nothing is touching the metal tip at the end. The soldering iron will get very hot very quickly! It’s important to handle this device with care. Turn the soldering iron on and wait for it to heat up. DO NOT HOLD THE SOLDERING IRON BY THE TIP, YOU WILL BURN YOURSELF. Always grab the soldering iron by its heat insulated padding.

### 4. Assembling the LED ring part 1

The cathode will be colour coded black and the anode will be colour coded red on the LEDs. It is extremely important that the LED is
colour coded and soldered correctly in the next steps or else the LED
may not light up!

Connect two LEDs together by soldering their cathodes together with a black wire segment and their anodes with a red wire segment. Repeat this step twice to end up with two two-LED circuits.

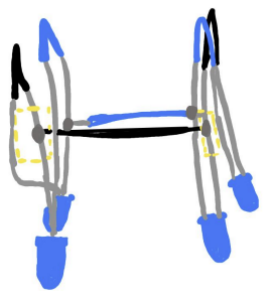
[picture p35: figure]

### 5. Assembling The LED Ring part 2

Use the remaining black wire segment to bridge the cathodes of the two LED pairs together. Then, using the red wire segment, bridge the anodes of the same two LEDs or of the other two LEDs. This will result in either a U-shaped or O-shaped LED circuit where all four LEDs are connected in parallel.

### 6. Adding a connector to the LED assembly

To make the LED rings detachable (and thus replaceable), a connector is needed. Create a new set of red and black wires with a female dupont connector on one end, and a stripped end. Solder the stripped end of the red connector wire to the anode of one of the LEDs in the assembly, and the black connector wire
to the cathode of another LED in the assembly.

For a U-shaped arrangement, we recommend soldering the connector wires to the two free-hanging LEDs. For the O-shaped arrangement, the connector wires can be soldered to any two adjacent LEDs.

Repeat steps 2 through 6 to create three more LED assemblies for one RECORD arena.

### 7. Preparing for the LED cable

Cut four long segments of two-conductor copper
speaker cable and strip about 1 cm of the inside

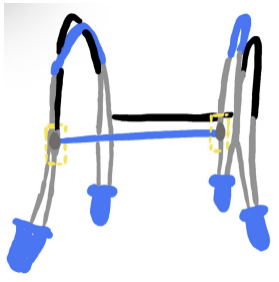
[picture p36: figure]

black and red wires at both ends. The segments should be long enough to put some amount of distance between the RECORD electronics and the RECORD arena. It is recommended that this distance is measured beforehand and to add about 1 metre to it for slack.

### 8. Creating the JST connector end of the cable

On one end of the four cables, twist and solder the four black wires together, then solder an additional wire to the end of this joint.

Create five wires with a JST connector pin on one end and strip the other end.

Solder the red speaker wires to four of these wires and insert them into pins 1 through 4 of the JST-XH connector housing.
Solder the black speaker wire bundle to the last connector wire and insert it into pin 6 of the JST-XH connector housing.

Put this end of the wire aside for now.

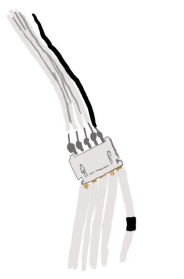
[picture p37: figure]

### 9. Creating the LED assembly connector

On the other end, a male dupont connection for an LED assembly must be made for each cable. Solder a red male dupont wire to the red speaker wire and a black male dupont wire to the black speaker wire. Wrap any exposed solder joints with electrical tape.

### 10. Testing connection continuity

Connect the LED assemblies to the dupont connector end of the completed LED cable. Use the multimeter to test continuity between the connected LED terminals and each pin of the JST-XH connector. Keep track of which cable corresponds to which LED assembly and label the wire and LEDs appropriately.

# Valves and valve cables

CAUTION: You will be working with very hot equipment in this section. Please make sure you take the proper precautions to not burn yourself, other team members, or any objects inside and outside of your work area!

The solenoid valves are involved in reward (food) delivery to the animal in the arena. These valves are driven by 20 - 25 Volts direct current (DC) which will be delivered by an external power source. By the end of this section, you should have a set of four valves and a valve cable with a 6-position female JST-XH connector.

## Materials

- 4 Solenoid Valves
- Speaker cable
- 1 Six-position female JST-XH connector
- Dupont wire (female)

- Dupont wire (male)
- A soldering iron
- Solder
- Wire strippers
- Wire cutters
- And a Multimeter

### 1. Preparing the cable

Using the wire cutters, measure and cut a section of speaker cable for each valve, to end up with 4 segments of speaker cable. The segments should be long enough to put some amount of distance between the RECORD electronics and the RECORD arena. It is recommended that this distance is measured beforehand and to add about 1 metre to it for slack.
Strip both ends of the speaker wire. One end will need female dupont connectors and the other will be housed by a 5-pin JST-XH connector.

Prepare 4 wires with one female dupont connector each, 8 with a male dupont connector, and 5 with an XH pin on one end. The other end of each of these wires should be stripped and prepared for soldering.

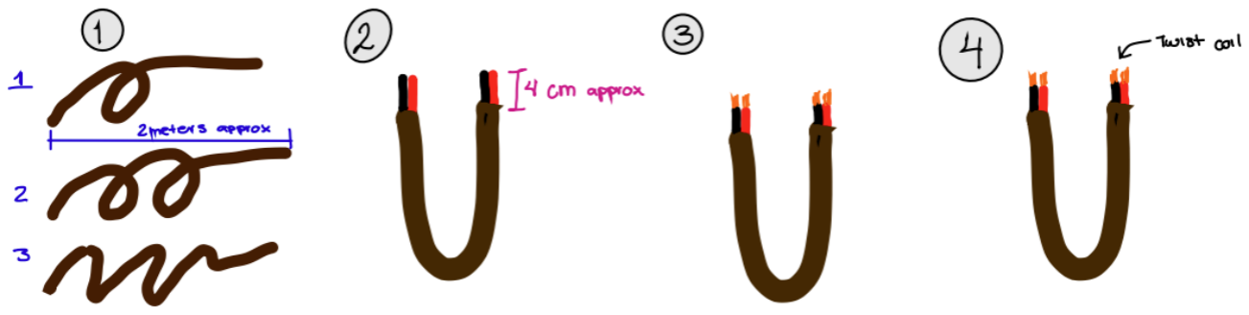
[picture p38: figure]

### 2. Soldering Preparation

Make sure the soldering iron is resting in its holder and nothing is touching the metal tip at the end. The soldering iron will get very hot very quickly! It’s important to handle this device with care. Turn the soldering iron on and wait for it to heat up. DO NOT HOLD THE SOLDERING IRON BY THE TIP, YOU WILL BURN YOURSELF. Always grab the soldering iron by its heat insulated padding.

### 3. Soldering connector wires to the valve

Each valve has three terminals, two on the top and one on the bottom. Solder the stripped end of two male dupont connector wires to one each one of the top terminals. Because the valves are not polarised, colour coding is not required.

### 4. Creating the connector on the wire

As with the LED cables, twist the four internal black wires on one end of the stripped speaker wire and solder them together, then solder a wire with an XH pin to the end of this joint. Then, solder one wire with an XH pin to each of the internal red wires on the same end of the speaker cable. All valves will be sharing one ground through one terminal, and will be supplied with power through the other terminal.

On the other end of the cable, solder a female dupont connector wire to each of the internal speaker wires.

Lastly, introduce the five XH pin wires into the JST-XT housing. Pin 5 will house the 4-wire joint wire and pins 1 through 4 will house the remaining wires.

### 5. Testing connection continuity

Connect the valves to the dupont connector end of the completed valve cable. Use the multimeter to test continuity between the connected valve terminals and each pin of the JST-XH connector. Keep track of which cable corresponds to which valve and label the wire and valves appropriately.

# Power and synchronisation cables

The power cable in the record system simply supplies the valves with the power they need to operate. This is done by connecting the cable to the RECORD circuit board, which in turn supplies that voltage to the relays that open and close the circuit that carries the external power source voltage. The synchronisation cables on the other hand simply serve as a link between the RECORD system and an external system. How the synchronisation cables are built will vary with respect to the external system that is in use, but the end of the cable that connects to RECORD will be the same.

Herein we will explain how to build synchronisation cables for the Noldus Ethovision system and the Inscopix nVista DAQ box system.

## Materials

- Speaker wire (x 1)
- Cat 5 cable (Noldus) (x 1)
- Coaxial cable (Inscopix) (x 1)
- Dupont wire or dupont connectors crimpable pins and housings (2 female, 2 male)
- 2-position JST-XH connector housing (x 2)
- XH crimpable pins (x 4)
- Soldering iron and solder
- Wire cutters

- Wire strippers (0.80 - 2.6 mm² , AWG 10-20)
- Crimper (0.1 - 0.5 mm²
, AWG 26-20)

## Power cable

### 1. Preparing the cable

Using the wire cutters, measure and cut a section of speaker cable. The segment should be long enough to put some amount of distance between the RECORD electronics and power supply. It is recommended that this distance is measured beforehand and to add about 1 metre to it for slack.
Strip both ends of the speaker wire. One end will need male dupont connectors and the other will be housed by a 2-pin JST-XH connector.

Prepare 2 wires with one male dupont connector each and 2 with an XH pin on one end. The other end of each of these wires should be stripped and prepared for soldering. Alternatively, the pins and connectors may be crimped onto the speaker wire directly if the wire is small enough to fit in the crimp.

### 2. Soldering Preparation

Make sure the soldering iron is resting in its holder and nothing is touching the metal tip at the end. The soldering iron will get very hot very quickly! It’s important to handle this device with care. Turn the soldering iron on and wait for it to heat up. DO NOT HOLD THE SOLDERING IRON BY THE TIP, YOU WILL BURN YOURSELF. Always grab the soldering iron by its heat insulated padding.

### 3. Creating the connectors on the wire

Solder a wire or crimp an XH connector pin to each of the internal wires on one end of the speaker cable. Make one of these wires as “GROUND” and make sure to keep track of it.

On the other end of the cable, solder or crimp a male dupont connector to both of the internal speaker wires.

Lastly, introduce the two XH pin wires into the JST-XT housing. Pin 5 will house the 4-wire joint wire and pins 1 through 4 will house the remaining wires.

### 4. Identify the appropriate wires on the Noldus synchronisation cable

Using the following diagram, taken from the “USB-IO box / Mini USB-IO box for EthoVision XT 13.0” reference guide, identify and solder the female dupont wires to “Add-On Supply V+ 18 Volt” and “ground” and connect them to the cable you just made.

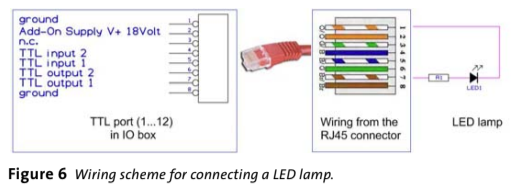
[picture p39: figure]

## Noldus synchronisation cable

### 1. Preparing the cable

Follow the same steps followed for the power cable, but instead of using male dupont connectors, use female connectors. This will create a detachable interface between the RECORD system’s cable and the Noldus sync cable.

Because the Noldus I/O box uses ethernet connections, we will be using a CAT5 cable for synchronisation. Expose the ends of each internal wire in the CAT5 cable to prepare them for soldering/crimping.

### 2. Identify the CAT5 wires

Using the following diagram, taken from the “USB-IO box / Mini USB-IO box for EthoVision XT 13.0” reference guide, identify and solder the male dupont wires to “TTL input 1” and ground and connect them to the cable prepared in step 1. Solder additional wires if needed, but be sure to make more sync cables for any other TTL being used.

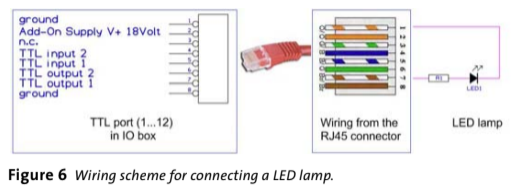
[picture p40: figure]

## Inscopix synchronisation cable

### 1. Preparing the cable

Using the wire cutters, measure and cut a section of coaxial cable. The segment should be long enough to put some amount of distance between the RECORD electronics and power supply. It is recommended that this distance is measured beforehand and to add about 1 metre to it for slack.
Expose the internals of this cable. The outer shielding will need to be grounded and the internal conductor will carry the TTL signal.

You’ll need a wire with an XH pin crimped onto it and a wire with a female dupont connector for this build. The other end of each of these wires should be stripped and prepared for soldering.

### 5. Soldering Preparation

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

### 6. Creating the connectors on the wire

Solder the XH wire to the internal conductor of the coax cable, then solder the dupont wire to the wire that wraps around the coax shielding. Mark the dupont wire as “GROUND”. Wrap all exposed cable internals with electrical tape, making sure that the shielding wire does not touch the internal conductor wire, then insert the XH wire into the JST-XH housing.

### 7. Grounding the coaxial shielding

Connect the dupont wire that was soldered to the shielding wire on the coax cable directly to a GROUND pin on the microcontroller. This will ensure that the TTL signal is clean and does not float.

# Hardware connections

## Microcontroller

The microcontroller unit (MCU) provides control for all electronic components in the RECORD system (excluding any external spatial tracking software). The following table and figure describe the pin that drives each electronic component. All connections from the MCU to its respective component listen on the table below (with the exception of the eUSCI pins) are indirect, as they pass first through the printed circuit board (PCB). We use the Texas Instruments MSP-EXP430FR2355 launchpad development kit (https://www.ti.com/tool/MSP-EXP430FR2355). For additional documentation on this microcontroller, please visit the manufacturers website (https://www.ti.com/product/MSP430FR2355).

Peripheral Type | Associated Electronic Component | Pin on MSP430-FR2355 Launchpad
GPIO | TTL out (ACK signal) | P3.0
GPIO | Relay 1 or 5 | P3.1
GPIO | Relay 2 or 6 | P3.2
GPIO | Relay 3 or 7 | P3.7
GPIO | Relay 4 or 8 | P3.4
GPIO | TTL in (SYNC signal) | P3.5
Capture/Compare Output, Timer B1 (PWM) | Cost LED Ring 1 | P6.0
Capture/Compare Output, Timer B2 (PWM) | Cost LED Ring 2 | P6.1
Capture/Compare Output, Timer B3 (PWM) | Cost LED Ring 3 | P6.2
Capture/Compare Output, Timer B4 (PWM) | Cost LED Ring 4 | P6.3
Capture/Compare Output, Timer B5 (PWM) | Trial Indicator LED | P6.4
eUSCI, UART RXD | Serial Communication Receive | P1.6
eUSCI, UART TXD | Serial Communication Transmit | P1.7

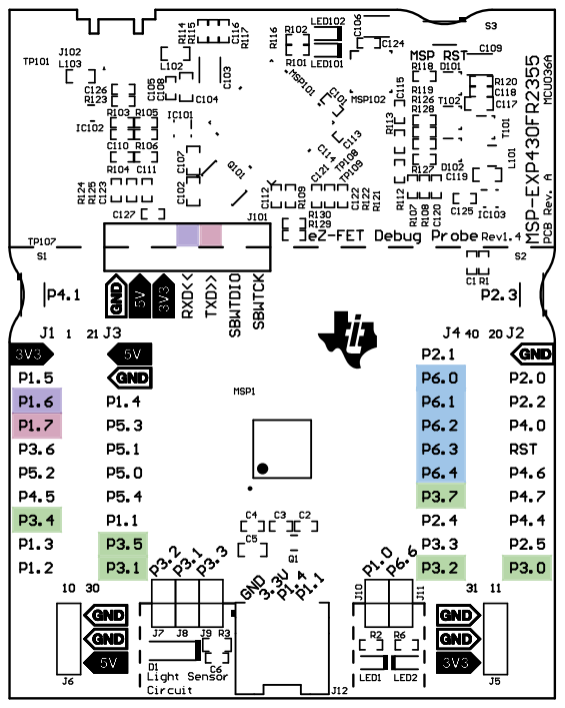
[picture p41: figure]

PCB layout image credit to Texas Instruments. https://www.ti.com/tool/MSP-EXP430FR2355#design-files (SLAR152.zip, “MSP-EXP430FR2355_PCBlayers.pdf” pg. 1)

## Relay Shield

### Position on Relay Shield

### Connection on PCB Name

### (For each relay)

VCC | H4.9 | Positive power supply
GND | H4.10 | Ground
NO | CONN7.x / CONN8.x | Normally open terminal
NC | Not Connected | Normally closed terminal
COM | CONN9.x / CONN10.x | Common voltage terminal
INx (1 through 8) | H4.x (1 through 8) | Input trigger signal terminal

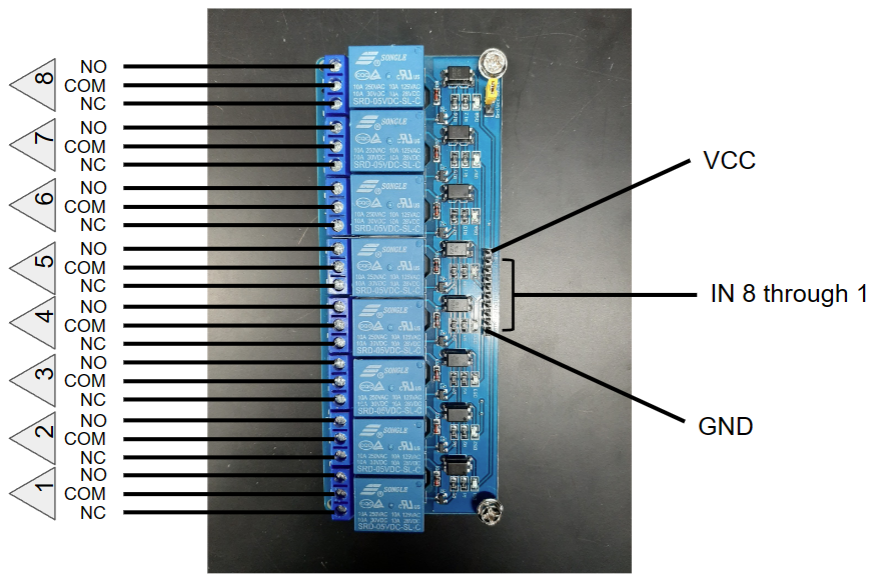
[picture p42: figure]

## Printed Circuit Board (PCB)

The PCB can relay up to two different RECORD microcontroller inputs and outputs, or drive up to eight cost/reward components from a single microcontroller, if the firmware and hardware allow it. No cost/reward components are connected directly to the microcontroller, rather, they are connected to the PCB to be held tightly in place, while the PCB is connected to the microcontroller through jumper wires. See “Microcontroller, Relay, and PCB connections” for a detailed connection table.

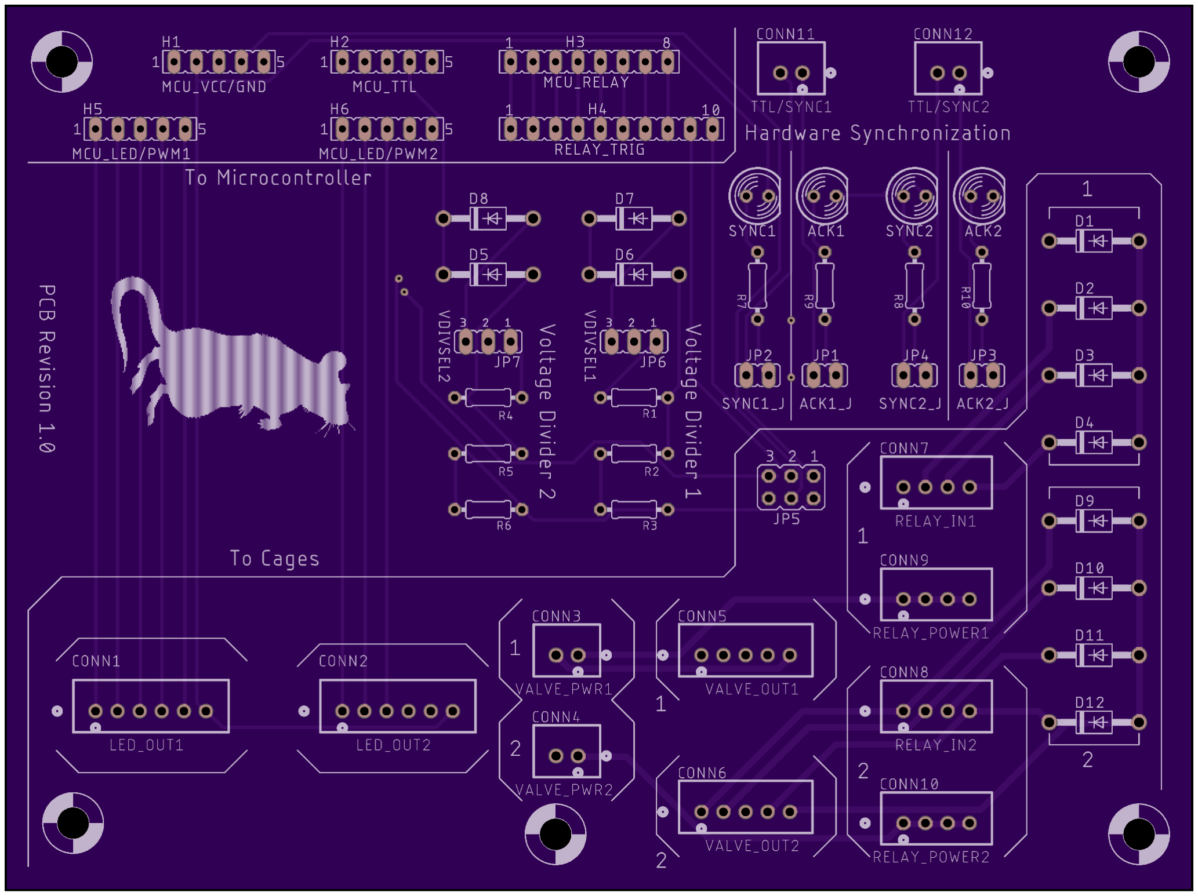
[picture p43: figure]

Custom RECORD PCB, Revision 1.0

### PCB schematics

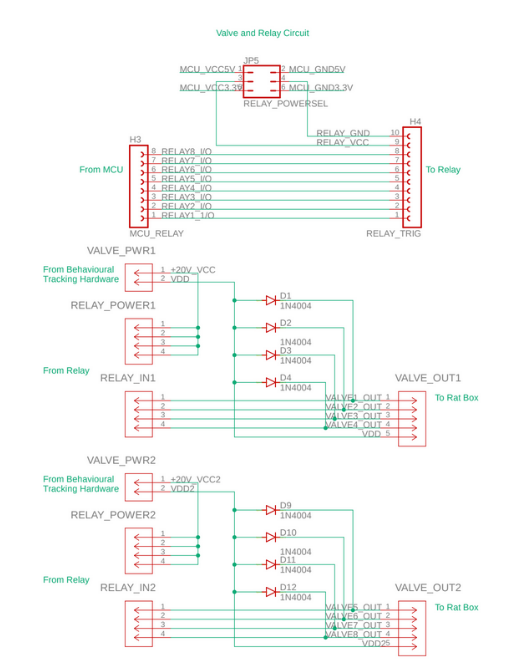
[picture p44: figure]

Custom RECORD PCB schematic, generated in Autodesk Eagle, PCB Revision 1.0

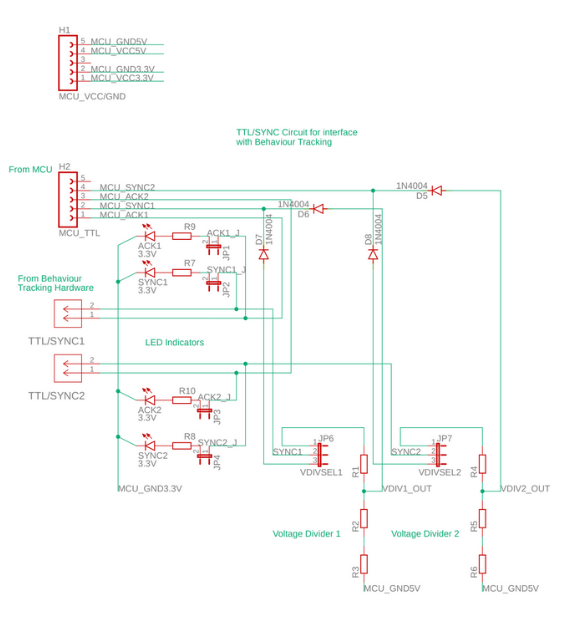
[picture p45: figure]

Custom RECORD PCB schematic, generated in Autodesk Eagle, PCB Revision 1.0

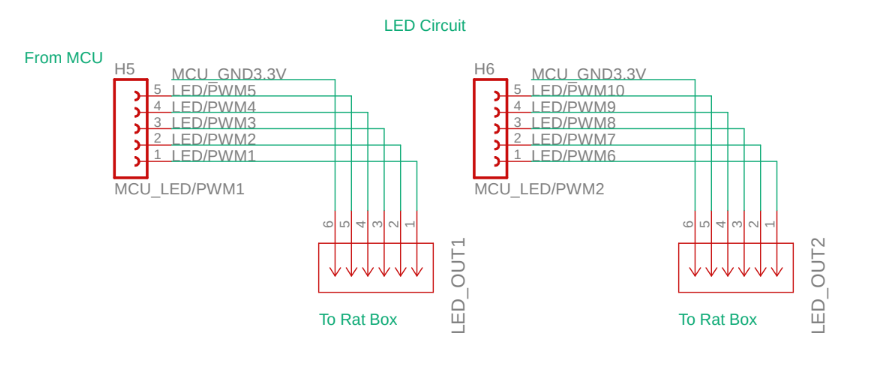
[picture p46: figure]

Custom RECORD PCB schematic, generated in Autodesk Eagle, PCB Revision 1.0

## List of components

PCB Position | Manufacturer | Part Number | Value | Units | Component type
R1* | Sparkfun | COM-10969 | 2.2* ± 5 | kΩ % | Resistor
R2* | Sparkfun | COM-10969 | 3.3* ± 5 | kΩ % | Resistor
R3* | Sparkfun | COM-10969 | 0* | Ω | Resistor
R4* | Sparkfun | COM-10969 | 2.2* ± 5 | kΩ % | Resistor
R5* | Sparkfun | COM-10969 | 3.3* ± 5 | kΩ % | Resistor
R6* | Sparkfun | COM-10969 | 0* | Ω | Resistor
R7* | Sparkfun | COM-10969 | 0* | Ω | Resistor
R8* | Sparkfun | COM-10969 | 0* | Ω | Resistor
R9* | Sparkfun | COM-10969 | 0* | Ω | Resistor
R10* | Sparkfun | COM-10969 | 0* | Ω | Resistor
D1 | Vishay General Semiconducto rs | 1N4007E-E3 /54 | Vf = 1.1 Vr = 1000 | V | Diode
D2 | Vishay General Semiconducto rs | 1N4007E-E3 /54 | Vf = 1.1 Vr = 1000 | V | Diode
D3 | Vishay General Semiconducto rs | 1N4007E-E3 /54 | Vf = 1.1 Vr = 1000 | V | Diode
D4 | Vishay General Semiconducto rs | 1N4007E-E3 /54 | Vf = 1.1 Vr = 1000 | V | Diode
D5 | Vishay General | 1N4007E-E3 /54 | Vf = 1.1 Vr = 1000 | V | Diode

| Semiconducto rs
D6 | Vishay General Semiconducto rs | 1N4007E-E3 /54 | Vf = 1.1 Vr = 1000 | V | Diode
D7 | Vishay General Semiconducto rs | 1N4007E-E3 /54 | Vf = 1.1 Vr = 1000 | V | Diode
D8 | Vishay General Semiconducto rs | 1N4007E-E3 /54 | Vf = 1.1 Vr = 1000 | V | Diode
D10 | Vishay General Semiconducto rs | 1N4007E-E3 /54 | Vf = 1.1 Vr = 1000 | V | Diode
D11 | Vishay General Semiconducto rs | 1N4007E-E3 /54 | Vf = 1.1 Vr = 1000 | V | Diode
D12 | Vishay General Semiconducto rs | 1N4007E-E3 /54 | Vf = 1.1 Vr = 1000 | V | Diode
H1 | Samtec Inc | TSW-105-07 -T-S | Pitch = 2.54 Position = 5 | mm | Board to Board Header
H2 | Samtec Inc | TSW-105-07 -T-S | Pitch = 2.54 Position = 5 | mm | Board to Board Header
H3 | Samtec Inc | TSW-108-07 -T-S | Pitch = 2.54 Position = 8 | mm | Board to Board Header
H4 | Samtec Inc | TSW-110-07-T-S | Pitch = 2.54 Position = 10 | mm | Board to Board Header
H5 | Samtec Inc | TSW-105-07 -T-S | Pitch = 2.54 Position = 5 | mm | Board to Board

| | | | | Header
H6 | Samtec Inc | TSW-105-07 -T-S | Pitch = 2.54 Position = 5 | mm | Board to Board Header
JP1 | Samtec Inc | TSW-102-07 -T-S | Pitch = 2.54 Position = 2 | mm | Board to Board Header
JP2 | Samtec Inc | TSW-102-07 -T-S | Pitch = 2.54 Position = 2 | mm | Board to Board Header
JP3 | Samtec Inc | TSW-102-07 -T-S | Pitch = 2.54 Position = 2 | mm | Board to Board Header
JP4 | Samtec Inc | TSW-102-07 -T-S | Pitch = 2.54 Position = 2 | mm | Board to Board Header
JP5 | Samtec Inc | TSW-103-07 -T-S | Pitch = 2.54 Position = 3 Rows = 2 | mm | Board to Board Header
JP6 | Samtec Inc | TSW-103-07 -T-S | Pitch = 2.54 Position = 3 | mm | Board to Board Header
JP7 | Samtec Inc | TSW-103-07 -T-S | Pitch = 2.54 Position = 3 | mm | Board to Board Header
CONN1 | Qibaok | XH-6A | Pitch = 2.54 Female Position = 6 | mm | JST-XH Female Header
CONN2 | Qibaok | XH-6A | Pitch = 2.54 Female Position = 6 | mm | JST-XH Female Header
CONN3 | Qibaok | XH-2A | Pitch = 2.54 Female Position = 2 | mm | JST-XH Female Header
CONN4 | Qibaok | XH-2A | Pitch = 2.54 Female Position = 2 | mm | JST-XH Female Header
CONN5 | Qibaok | XH-5A | Pitch = 2.54 | mm | JST-XH

| | | Female Position = 5 | | Female Header
CONN6 | Qibaok | XH-5A | Pitch = 2.54 Female Position = 5 | mm | JST-XH Female Header
CONN7 | Qibaok | XH-4A | Pitch = 2.54 Female Position = 4 | mm | JST-XH Female Header
CONN8 | Qibaok | XH-4A | Pitch = 2.54 Female Position = 4 | mm | JST-XH Female Header
CONN9 | Qibaok | XH-4A | Pitch = 2.54 Female Position = 4 | mm | JST-XH Female Header
CONN10 | Qibaok | XH-4A | Pitch = 2.54 Female Position = 4 | mm | JST-XH Female Header
CONN11 | Qibaok | XH-2A | Pitch = 2.54 Female Position = 2 | mm | JST-XH Female Header
CONN12 | Qibaok | XH-2A | Pitch = 2.54 Female Position = 2 | mm | JST-XH Female Header
SYNC1* | Kingbright Company LLC | WP7113VBC /D | Vf = 3.3** Lens = 5 | V mm | Light Emitting Diode (LED)
ACK1* | Kingbright Company LLC | WP7113VBC /D | Vf = 3.3** Lens = 5 | V mm | Light Emitting Diode (LED)
SYNC2* | Kingbright Company LLC | WP7113VBC /D | Vf = 3.3** Lens = 5 | V mm | Light Emitting Diode (LED)
ACK2* | Kingbright Company LLC | WP7113VBC /D | Vf = 3.3** Lens = 5 | V mm | Light Emitting Diode (LED)

* Components and values reflect what was used for our particular setup. These Values should be chosen according to each system’s requirements
** Different LED forward voltages may be needed depending on each individual system. The LED should be able to turn on with its corresponding TTL signal voltages delivered by the microcontroller and voltage divider output. Voltage divider output is dependent on R1, R2, and R3 for SYNC1 and ACK1, as well as R4, R5, and R6 for SYNC2 and ACK2. Value shown is the typical operating voltage for the LED, see component datasheet for maximum and minimum forward voltages.

Internal Connectors:
Pictured in the image below (bottom right), they serve to connect the PCB to the relay shield input/outputs.
CONN7 | Qibaok | XH-4Y | Pitch = 2.54 Male Position = 4 | mm | JST-XH Male Connector
CONN8 | Qibaok | XH-4Y | Pitch = 2.54 Male Position = 4 | mm | JST-XH Male Connector
CONN9 | Qibaok | XH-4Y | Pitch = 2.54 Male Position = 4 | mm | JST-XH Male Connector
CONN10 | Qibaok | XH-4Y | Pitch = 2.54 Male Position = 4 | mm | JST-XH Male Connector

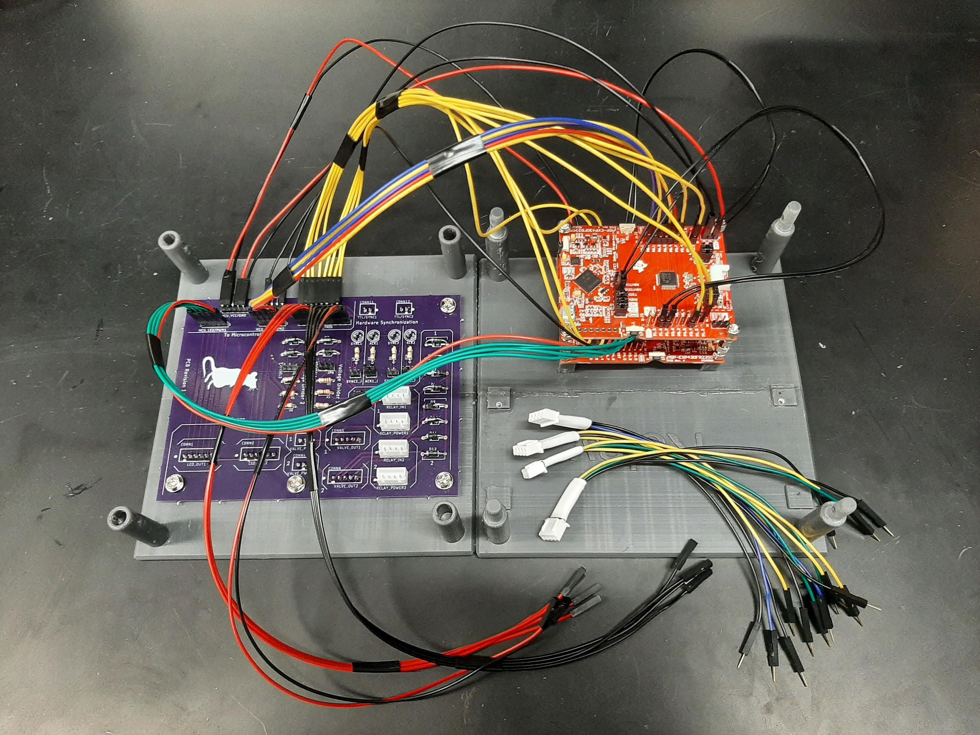
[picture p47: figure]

## Microcontroller, Relay, and PCB Connections

### Connections for MCU 1

Signal | Position on MCU (MSP430-FR2355) | Position on PCB | Position on Relay Shield
Cost LED1 | P6.0 | H5.1 | -
Cost LED2 | P6.1 | H5.2 | -
Cost LED3 | P6.2 | H5.3 | -
Cost LED4 | P6.3 | H5.4 | -
Trial Indicator LED | P6.4 | H5.5 | -
Low-Voltage Supply* | 3V3 or 5V* | H1.1 | -
Ground | GND | H1.2 | -
SYNC | P3.5 or P3.6*** | H2.1 | -
ACK | P3.0*** | H2.2 | -
Trigger Signal for Relay 1 | P3.1 | H3.1 | -
Trigger Signal for Relay 2 | P3.2 | H3.2 | -
Trigger Signal for Relay 3 | P3.7 | H3.3 | -
Trigger Signal for Relay 4 | P3.4 | H3.4 | -
MCU to Relay 1 | - | H4.1 | IN1
MCU to Relay 2 | - | H4.2 | IN2
MCU to Relay 3 | - | H4.3 | IN3
MCU to Relay 4 | - | H4.4 | IN4
Relay VCC | - | H4.9 | VCC
Relay GND | - | H4.10 | GND
Relay 1 to Valve 1 | - | CONN7.1 | Relay 1, Normally Open Terminal

Relay 2 to Valve 2 | - | CONN7.2 | Relay 2, Normally Open Terminal
Relay 3 to Valve 3 | - | CONN7.3 | Relay 3, Normally Open Terminal
Relay 4 to Valve 4 | - | CONN7.4 | Relay 4, Normally Open Terminal
Common High-voltage supply for valves 1 - 4 | - | CONN9.1-4** | Relay 1-4, COM Terminal

* Supplying low-voltage power to the PCB serves to route the voltage and ground to the relay shield. Make sure you are providing enough power to the relay shield and that the jumpers on JP5 are configured in the correct way to carry that voltage. The relay shield may be able to operate on 3.3V, however 5V is recommended.
** Connector 9 simply supplies voltage to the relay. The COM terminal is shorted with the Normally Open terminal when the relay is activated. The order in which the pins on the connector are connected to each relay’s COM terminal has no effect on the function of the system.
*** This connection depends on the particular use-case scenario. P3.0 is the outgoing ACK signal that pulses every time a command is executed, P3.5 is an user-triggerable outgoing TTL signal, and P3.6 is for incoming TTL signals. Incoming TTL signals must be stepped down to 3.3V to not damage the system. Care must be taken when selecting what should be connected where.

### Connections for MCU 2

Signal | Position on MCU | Position on PCB | Position on Relay Shield
Cost LED1 | P6.0 | H6.1 | -
Cost LED2 | P6.1 | H6.2 | -
Cost LED3 | P6.2 | H6.3 | -
Cost LED4 | P6.3 | H6.4 | -
Trial Indicator LED | P6.4 | H6.5 | -
Low-Voltage Supply* | 3V3 or 5V* | H1.3 | -
Ground | GND | H1.4 | -
SYNC | P3.5 or P3.6*** | H2.4 | -
ACK | P3.0*** | H2.5 | -
Trigger Signal for Relay 1 | P3.1 | H3.5 | -
Trigger Signal for Relay 2 | P3.2 | H3.6 | -
Trigger Signal for Relay 3 | P3.7 | H3.7 | -
Trigger Signal for Relay 4 | P3.4 | H3.8 | -
MCU to Relay 1 | - | H4.5 | IN5
MCU to Relay 2 | - | H4.6 | IN6
MCU to Relay 3 | - | H4.7 | IN7
MCU to Relay 4 | - | H4.8 | IN8
Relay VCC | - | H4.9 | VCC
Relay GND | - | H4.10 | GND
Relay 5 to Valve 1 | - | CONN8.1 | Relay 5, Normally Open Terminal
Relay 6 to Valve 2 | - | CONN8.2 | Relay 6, Normally Open Terminal

Relay 7 to Valve 3 | - | CONN8.3 | Relay 7, Normally Open Terminal
Relay 8 to Valve 4 | - | CONN8.4 | Relay 8, Normally Open Terminal
Common High-voltage supply for valves 1 - 4 | - | CONN10.1-4** | Relay 5-8, COM Terminal

* Supplying low-voltage power to the PCB serves to route the voltage and ground to the relay shield. Make sure you are providing enough power to the relay shield and that the jumpers on JP5 are configured in the correct way to carry that voltage. The relay shield may be able to operate on 3.3V, however 5V is recommended.
** Connector 10 simply supplies voltage to the relay. The COM terminal is shorted with the Normally Open terminal when the relay is activated. The order in which the pins on the connector are connected to each relay’s COM terminal has no effect on the function of the system.
*** This connection depends on the particular use-case scenario. P3.0 is the outgoing ACK signal that pulses every time a command is executed, P3.5 is an user-triggerable outgoing TTL signal, and P3.6 is for incoming TTL signals. Incoming TTL signals must be stepped down to 3.3V to not damage the system.

# Resource table

[Under construction]

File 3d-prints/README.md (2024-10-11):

# Welcome to RECORD/3dprinting!
The section contains all the 3D printing files needed for the RECORD system's arenas, as well as miscellaneous components we ended up making. Every piece can be downloaded and printed directly with the STL file, or edited with the CAD files provided.

All CAD files were created in [Autodesk AutoCAD](https://www.autodesk.com/products/autocad). However, in spirit of keeping everything open-source and accessible, we recommend using [FreeCAD](https://www.freecad.org/) and a [DWG file importer](https://wiki.freecad.org/FreeCAD_and_DWG_Import) for modifying these CAD files, or alternatively [Blender](https://www.blender.org/) if you wish to work with the STLs directly.

## Designed with modularity and scalability in mind
The RECORD arenas are designed to be customisable and reconfigurable. We have validated our system using a square arena with reward sites at each corner, but the shape and size of the arena can be adjusted based on your lab's needs!

## Our dummy rat
The dummy rat we have used for testing animal detection efficacy can be found [here](https://www.thingiverse.com/thing:182233).

> Written with [StackEdit](https://stackedit.io/).
<!--stackedit_data:
eyJoaXN0b3J5IjpbLTE0OTU4OTI2NThdfQ==
-->

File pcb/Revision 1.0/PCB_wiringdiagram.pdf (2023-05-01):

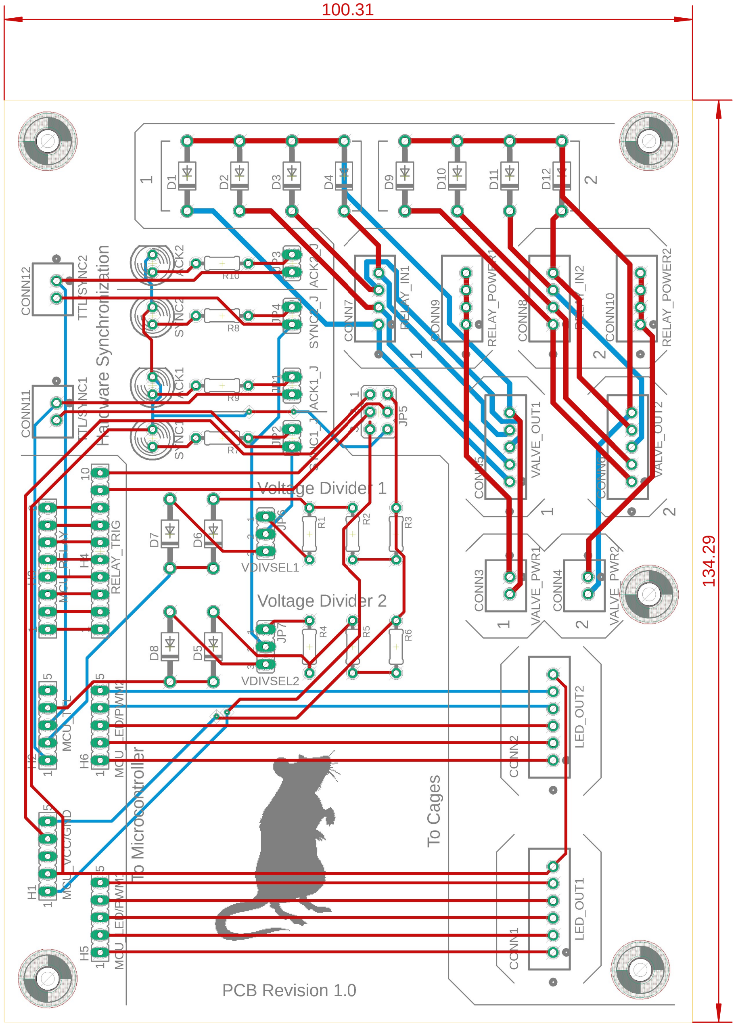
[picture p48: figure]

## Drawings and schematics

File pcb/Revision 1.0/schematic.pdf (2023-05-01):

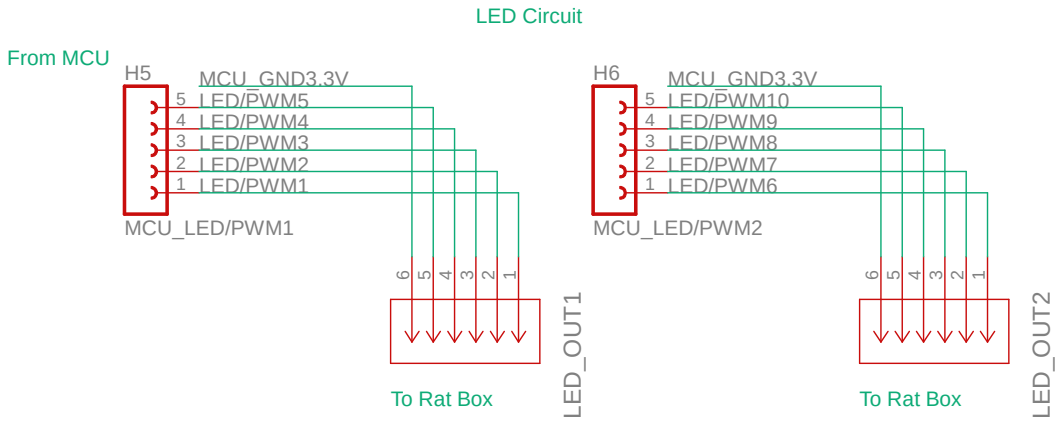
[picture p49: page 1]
MCU_LED/PWM1; MCU_LED/PWM2; 1 LED_OUT1; 1 LED_OUT2; 5 MCU_GND3.3V; MCU_GND3.3V H6; LED/PWM5 LED/PWM4 LED/PWM3 LED/PWM2 LED/PWM1; LED/PWM10 LED/PWM9 LED/PWM8 LED/PWM7 LED/PWM6; From MCU; LED Circuit

To Rat Box

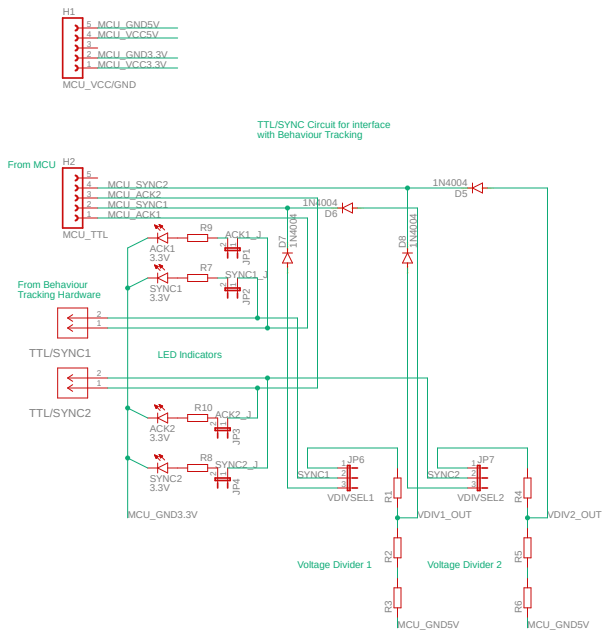
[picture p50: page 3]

TTL/SYNC Circuit for interface
with Behaviour Tracking

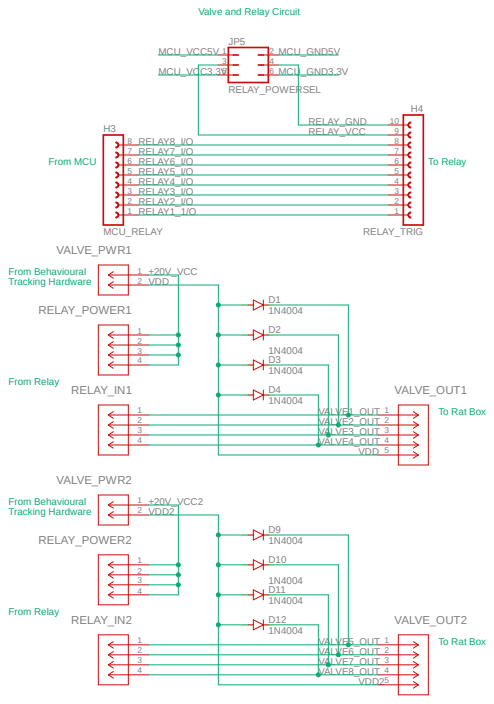
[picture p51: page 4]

Valve and Relay Circuit

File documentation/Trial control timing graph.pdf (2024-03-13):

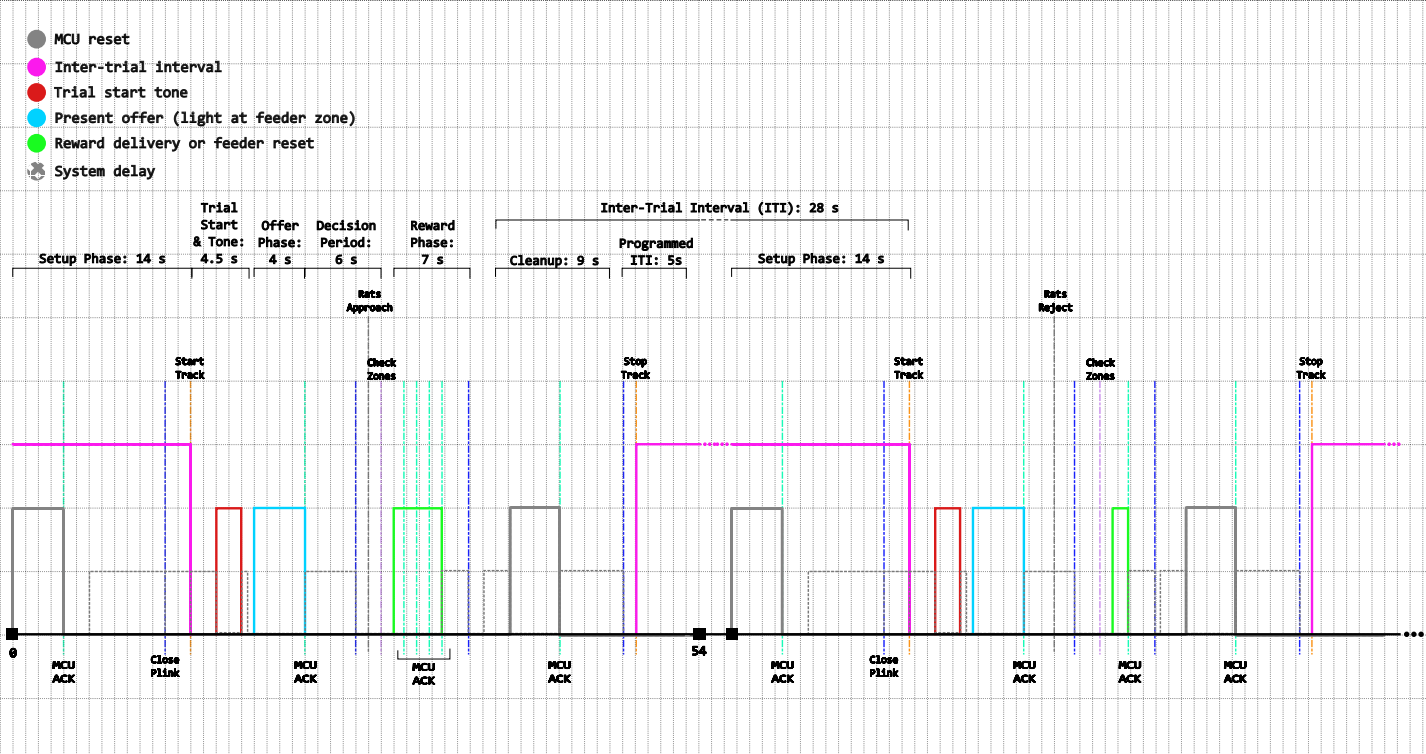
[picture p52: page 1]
54 MCU; ACK; Close Plink; MCU ACK; Trial; Inter-Trial; Interval; (ITI):; Inter-trial; interval; start; tone

MCU | reset

Present | | offer | (light | | | at | feeder | | zone)
Reward delivery or feeder System delay | | | | | | | | reset

& | Start Tone: | | Offer Phase: | | | Decision Period: | Reward Phase:

Programmed

Setup | Phase: | | 14 | s | | 4.5 | s | 4 | s | 6 | s Approach | Rats | | 7 | s | Cleanup: | 9 | s | ITI: | 5s | Setup | Phase: | 14 | s | | Rats Reject

Start Track | | | | | | | | Check Zones | | | | | | Stop Track | | | | | | Start Track | | Check Zones | Stop Track

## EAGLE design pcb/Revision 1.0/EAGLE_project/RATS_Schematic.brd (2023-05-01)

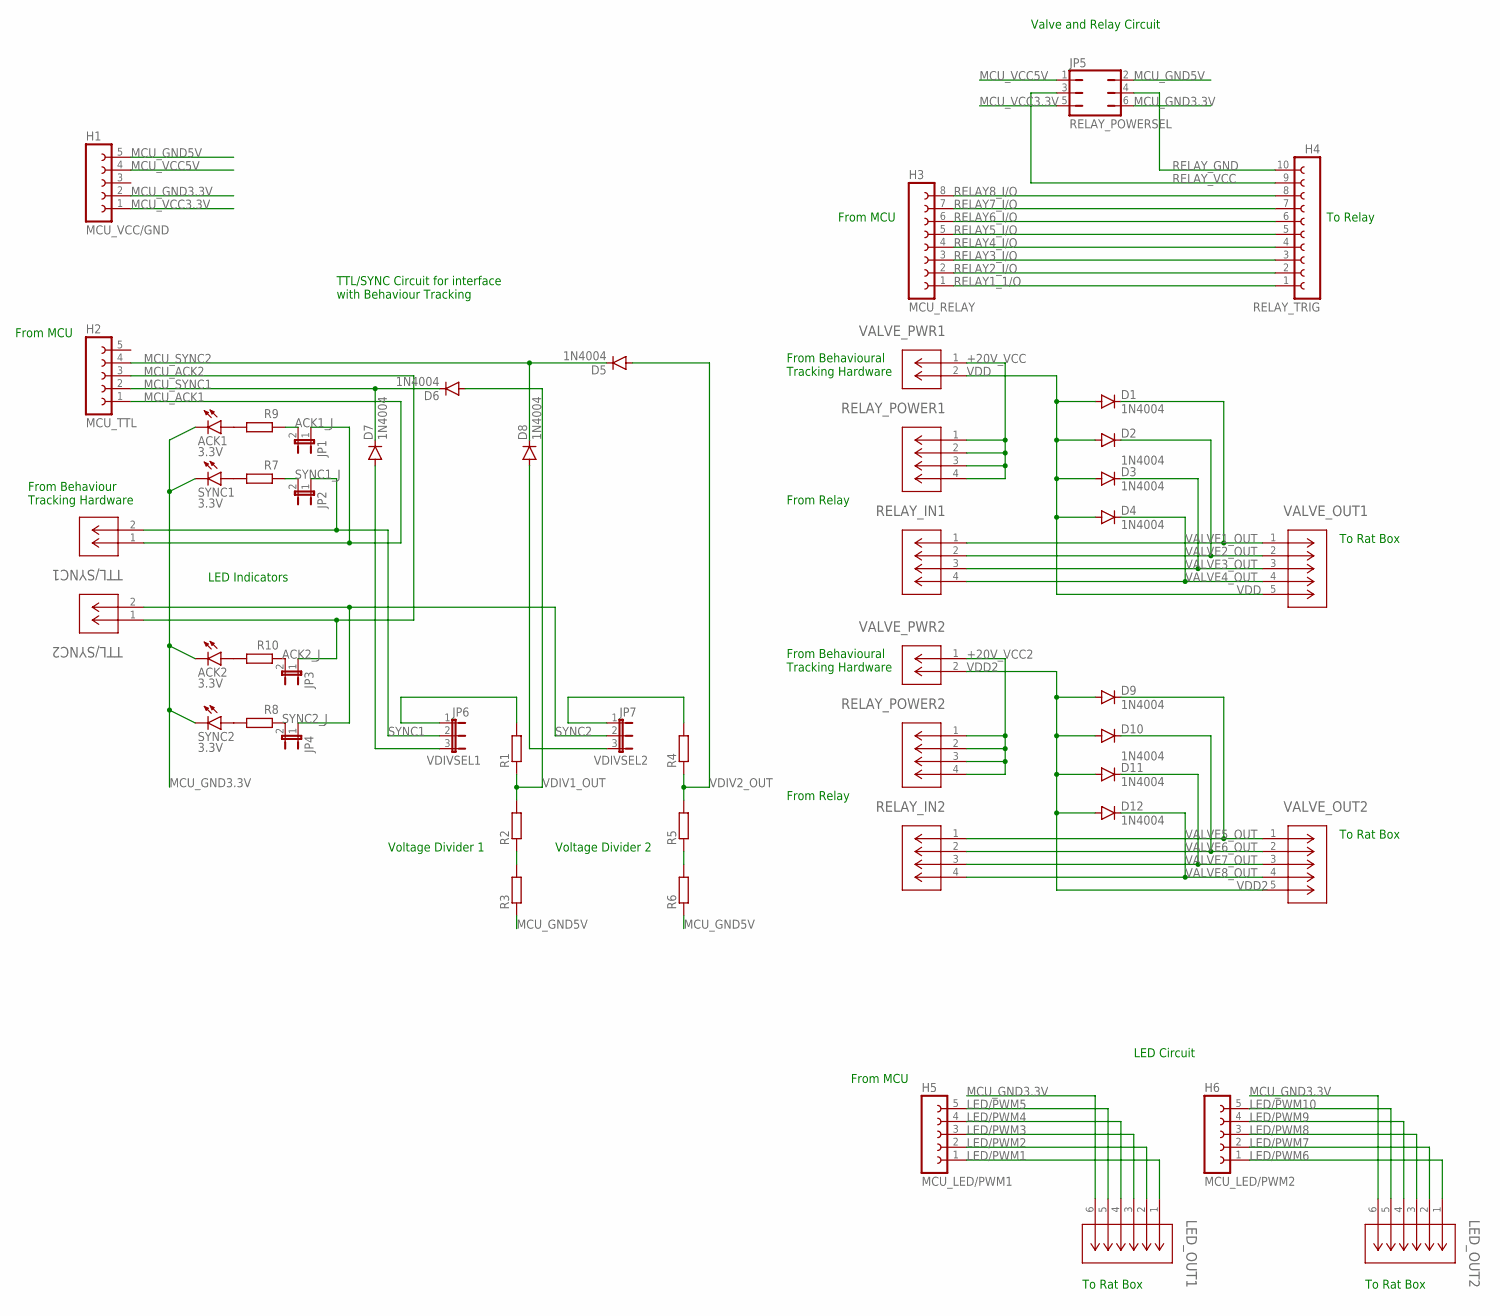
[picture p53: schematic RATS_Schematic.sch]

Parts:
ACK1, ACK2: 3.3V; LED5MM
D1, D2, D3, D4, D5, D6, D7, D8, D9, D10, D11, D12: 1N4004; DO41-10
H1: MCU_VCC/GND; FE05-1
H2: MCU_TTL; FE05-1
H3: MCU_RELAY; FE08
H4: RELAY_TRIG; FE10
H5: MCU_LED/PWM1; FE05-1
H6: MCU_LED/PWM2; FE05-1
JP1: ACK1_J; JP1
JP2: SYNC1_J; JP1
JP3: ACK2_J; JP1
JP4: SYNC2_J; JP1
JP5: RELAY_POWERSEL; JP3Q
JP6: VDIVSEL1; JP2
JP7: VDIVSEL2; JP2
LED_OUT1, LED_OUT2: B6B-XH-A(LF)(SN); CONN_B6B-XH-A(LF)(SN)_JST
R1, R2, R3, R4, R5, R6, R7, R8, R9, R10: R-EU_0204/7; 0204/7
RELAY_IN1, RELAY_IN2: B4B-XH-A_(LF)(SN); CONN_B4B-XH-A_(LF)(SN)_JST
RELAY_POWER1, RELAY_POWER2: B4B-XH-A_(LF)(SN); CONN_B4B-XH-A_(LF)(SN)_JST
SYNC1, SYNC2: 3.3V; LED5MM
TTL/SYNC1, TTL/SYNC2: B2B-XH-A(LF)(SN); CONN_B2B-XH-A(LF)(SN)_JST
VALVE_OUT1, VALVE_OUT2: B5B-XH-A(LF)(SN); CONN_B5B-XH-A(LF)(SN)_JST
VALVE_PWR1, VALVE_PWR2: B2B-XH-A(LF)(SN); CONN_B2B-XH-A(LF)(SN)_JST

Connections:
+20V_VCC: RELAY_POWER1.1, RELAY_POWER1.2, RELAY_POWER1.3, RELAY_POWER1.4, VALVE_PWR1.1
+20V_VCC2: RELAY_POWER2.1, RELAY_POWER2.2, RELAY_POWER2.3, RELAY_POWER2.4, VALVE_PWR2.1
LED/PWM1: H5.1, LED_OUT1.1
LED/PWM2: H5.2, LED_OUT1.2
LED/PWM3: H5.3, LED_OUT1.3
LED/PWM4: H5.4, LED_OUT1.4
LED/PWM5: H5.5, LED_OUT1.5
LED/PWM6: H6.1, LED_OUT2.1
LED/PWM7: H6.2, LED_OUT2.2
LED/PWM8: H6.3, LED_OUT2.3
LED/PWM9: H6.4, LED_OUT2.4
LED/PWM10: H6.5, LED_OUT2.5
MCU_ACK1: H2.1, JP1.1, TTL/SYNC1.1
MCU_ACK2: H2.3, JP3.1, TTL/SYNC2.1
MCU_GND3.3V: ACK1.K (C), ACK2.K (C), H1.2, JP5.6, LED_OUT1.6, LED_OUT2.6, SYNC1.K (C), SYNC2.K (C)
MCU_GND5V: H1.5, JP5.2, R3.1, R6.1
MCU_SYNC1: D6.C, D7.C, H2.2
MCU_SYNC2: D5.C, D8.C, H2.4
MCU_VCC3.3V: H1.1, JP5.5
MCU_VCC5V: H1.4, JP5.1
unnamed: R7.2, SYNC1.A
unnamed: R8.2, SYNC2.A
unnamed: R2.1, R3.2
unnamed: JP6.1, R1.2
unnamed: D7.A, JP6.3
unnamed: D8.A, JP7.3
unnamed: JP7.1, R4.2
unnamed: ACK1.A, R9.2
unnamed: R5.1, R6.2
unnamed: ACK2.A, R10.2
unnamed: JP2.2, R7.1
unnamed: JP1.2, R9.1
unnamed: JP3.2, R10.1
unnamed: JP4.2, R8.1
RELAY1_1/O: H3.1, H4.1
RELAY2_I/O: H3.2, H4.2
RELAY3_I/O: H3.3, H4.3
RELAY4_I/O: H3.4, H4.4
RELAY5_I/O: H3.5, H4.5
RELAY6_I/O: H3.6, H4.6
RELAY7_I/O: H3.7, H4.7
RELAY8_I/O: H3.8, H4.8
RELAY_GND: H4.10, JP5.4
RELAY_VCC: H4.9, JP5.3
SYNC1: JP2.1, JP6.2, TTL/SYNC1.2
SYNC2: JP4.1, JP7.2, TTL/SYNC2.2
VALVE1_OUT: D1.C, RELAY_IN1.1, VALVE_OUT1.1
VALVE2_OUT: D2.C, RELAY_IN1.2, VALVE_OUT1.2
VALVE3_OUT: D3.C, RELAY_IN1.3, VALVE_OUT1.3
VALVE4_OUT: D4.C, RELAY_IN1.4, VALVE_OUT1.4
VALVE5_OUT: D9.C, RELAY_IN2.1, VALVE_OUT2.1
VALVE6_OUT: D10.C, RELAY_IN2.2, VALVE_OUT2.2
VALVE7_OUT: D11.C, RELAY_IN2.3, VALVE_OUT2.3
VALVE8_OUT: D12.C, RELAY_IN2.4, VALVE_OUT2.4
VDD: D1.A, D2.A, D3.A, D4.A, VALVE_OUT1.5, VALVE_PWR1.2
VDD2: D9.A, D10.A, D11.A, D12.A, VALVE_OUT2.5, VALVE_PWR2.2
VDIV1_OUT: D6.A, R1.1, R2.2
VDIV2_OUT: D5.A, R4.1, R5.2

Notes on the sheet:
LED Indicators
From MCU
From Behaviour Tracking Hardware
Voltage Divider 1
Voltage Divider 2
From Behavioural Tracking Hardware
From Relay
To Relay
To Rat Box
TTL/SYNC Circuit for interface with Behaviour Tracking
Valve and Relay Circuit
LED Circuit

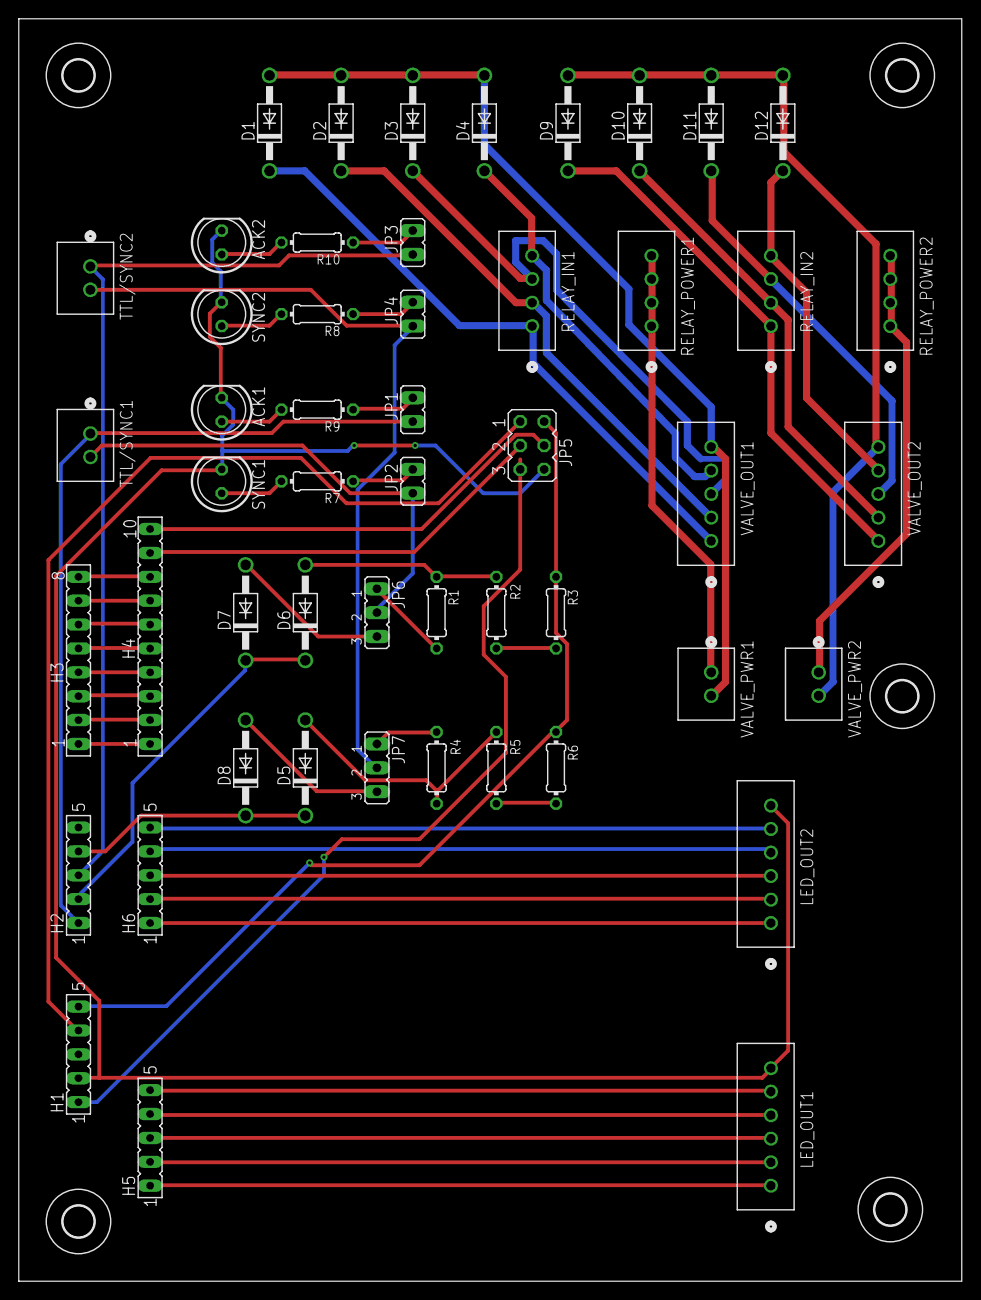
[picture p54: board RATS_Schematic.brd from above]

Board: 2 copper layers, 100.3 x 134.3 mm, 56 parts (0 on the bottom side), 58 nets.

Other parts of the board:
U$1, U$2, U$3, U$4, U$5: 3,3

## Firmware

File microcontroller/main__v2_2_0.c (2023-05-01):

/*
 * main.c
 *
 *  Created on: Mar 23, 2021
 *      Author: Raquel Ibáñez Alcalá
 *      Version: v2.2.0 (February 16, 2023)
 */

/****************************************************************************************************
 * MSP430-FR2355 R.E.C.O.R.D. (Reward-Cost in Rodent Decision-making) System Embedded Electronics
 *
 * Description: Proof of concept rodent arena controller for Friedman Lab rodent decision-making tasks.
 *  Communicates microcontroller with serial COM client running Windows 10 and connects to Noldus' TTL
 *  IO-Box. Microcontroller will receive commands from client called by Ethovision XT 16 and
 *  communicate back with a TTL pulse (ACK) after command finishes executing.
 *
 *                                                -------->| Inscopix TTL2_IN        |
 *                                               |   ----->| Inscopix TTL1_IN        |
 *                                               |  |       -------------------------
 *                                               |  |
 *                      MSP430FR2355             |  |            Noldus IO Box
 *             -------------------------------   |  |       -------------------------
 *            |                               |  |  |      |                         |
 *           <| P1.0 (LED1)      P3.0 (ACK)   |--|--o----->| TTL1_IN                 |
 *   PuTTY--->| P1.6 (UART RX)   P3.5 (TTL_IN)|<[]o--------| TTL1_OUT                |
 *   PuTTY<---| P1.7 (UART TX)   P3.6(TTL_OUT)|            |                         |
 *           >| P4.1 (SWITCH1)                |            |                         |
 *           >| P2.3 (SWITCH2)                |            |                         |
 *            |                               |            -------------------------
 *            |                               |                Open-Field Rodent Arena
 *            |                               |             -----------------------------
 *            |                               |            |                             |
 *            |                  P6.0 (TB3_1) |----------->| 1 Feeder1 LED ring          |
 *            |                  P6.1 (TB3_2) |----------->| 2 Feeder2 LED ring          |
 *            |                  P6.2 (TB3_3) |----------->| 3 Feeder3 LED ring          |
 *            |                  P6.3 (TB3_4) |----------->| 4 Feeder4 LED ring          |
 *            |                  P6.4 (TB3_5) |----------->| 5 Cue LED                   |
 *            |                  P3.1 (GPIO)  |---[Rly1]-->| 6 Valve 1                   |
 *            |                  P3.2 (GPIO)  |---[Rly2]-->| 7 Valve 2                   |
 *            |                  P3.7 (GPIO)  |---[Rly3]-->| 8 Valve 3                   |
 *            |                  P3.4 (GPIO)  |---[Rly4]-->| 9 Valve 4                   |
 *            |                               |            |                         GND |----< GND
 *            |                               |             -----------------------------
 *
 * Written by: Raquel Ibáñez Alcalá in March 2021 for Dr. Alexander Friedman
 * Version 2.2.0: 16 February 2023
 *
 ***************************************************************************************************/

#include <msp430.h>
#include <RECORD.h>
#include <stdio.h>
#include <stdlib.h>

void main(void)
{
    WDTCTL = WDTHOLD + WDTPW;   // Stop Watchdog timer

    /** ------ Calibrate clock ------ **/
    // Calibrate CPU clock to 8 MHz
    PM5CTL0 &= ~LOCKLPM5;       // Disable the GPIO power-on default high-impedance mode
                                // to activate 1previously configured port settings

    __bis_SR_register(SCG0);    // disable FLL
    CSCTL3 |= SELREF__REFOCLK;  // Set REFO as FLL reference source
    CSCTL1 = DCOFTRIMEN_1 |
             DCOFTRIM0    |
             DCOFTRIM1    |
             DCORSEL_3;         // DCOFTRIM=3, DCO Range = 8MHz
    CSCTL2 = FLLD_0 + 243;      // DCODIV = 8MHz
    __delay_cycles(3);
    __bic_SR_register(SCG0);    // enable FLL
    Software_Trim();            // Software Trim to get the best DCOFTRIM value

    CSCTL4 = SELMS__DCOCLKDIV |
             SELA__REFOCLK;     // set default REFO(~32768Hz) as ACLK source,
                                // default DCODIV as MCLK and SMCLK source


    /** ------ Setup GPIO ------ **/
    // Port 1
    P1DIR |= 0xFF;          // Set all pins on this port as output to start.
    P1OUT = 0x00;           // Turn all outputs off.

    P1SEL0 |= RXD | TXD;    // Set the UART pins to second function.
    P1SEL1 &= ~(RXD | TXD); // Make sure these bits are not set.

    // Port 2
    P2DIR |= 0xFF;          // Set all pins as output.
    P2OUT = 0x00;           // Set all outputs to 0

    // Port 3
    P3DIR |= 0xFF;          // Set all pins to output.
    P3OUT = 0x00;
    P3OUT |= RELAY1 | RELAY2    // Set these high for the relay array that toggles only when signal is low.
             | RELAY3 | RELAY4;
    P3DIR &= ~(TTL_IN);     // Input TTL signal for external TTLs.
    P3IES  &= ~(TTL_IN);    // Low to high input signal transition for input activation.

    // Port 4
    P4DIR |= 0xFF;          // Set all pins to output.
    P4OUT  = 0x00;          // Make sure they're all off.
    P4DIR &= ~(BTN1);       // Set on-board button 1 as input.
    P4IES &= ~(BTN1);       // Low to high input signal transition for interrupt activation.

    // Port 5
    P5DIR |= 0xFF;
    P5OUT = 0x00;

    // Port 6
    P6DIR |= 0xFF;
    P6OUT = 0x00;

    P6SEL0 |= ( TB3_1 |
                TB3_2 |
                TB3_3 |
                TB3_4 |
                TB3_5 );    // Select second function for these pins, Timer B3 for PWM.
    P6SEL1 &= ~( TB3_1 |
                 TB3_2 |
                 TB3_3 |
                 TB3_4 |
                 TB3_5 );   // Unset these bits.

    ButtonSetup();          // Optional internal button setup

    PM5CTL0 &= ~LOCKLPM5;   // Disable the GPIO power-on default high-impedance mode
                            // to activate previously configured port settings

    /** --- Setup RealTime Clock --- **/
    // The real time clock will be used to keep MCU time.
    // This peripheral will keep track of how long a command takes to execute, the value
    // will then be passed to the eUSCI peripheral to communicate this to a PC.

    // Source = Subsystem Master Clock (8 MHz, RTCSS), divided by 100 (80 kHz, RTCPS),
    // ensure software timer reset (RTCSR), and enable interrupts (RTCIE).
    // Start with clock disabled for now though. Set RTCSS bits to __SMCLK to activate.
    RTCCTL = RTCSS__DISABLED | RTCSR | RTCPS__100;

    // Set RTC count re-load compare value at 80 to get a tick every millisecond.
    // 100/8,000,000 * 80 = 0.001 sec.
    RTCMOD = 80-1;
    // Set both counting variables to 0.
    ms &= 0x0000;
    sc &= 0x0000;
    // Read the RTC Interrupt Vector register to reset RTC Interrupt Flag.
    if(RTCIV>0);

    /** ------ Setup Timer B1 ------ **/
    // This times is used for delays. Instead of using a busy wait with polling, we wish to put the system to sleep while closing a relay
    // or performing some other timed action such as raising a TTL signal.
    TB1CTL &= ~MC_3;        // Start with timer stopped. Mode referenced has no relevance to functionality, I'm just clearing the bits.
    TB1CTL |= TBSSEL_2;     // Select SMCLK source CONSIDER CHANGING THIS

    TB1CCTL0 |= CCIFG_0 | CCIE_1;     // Enable interrupts on this timer's capture compare module.
    TB1CCR0 = 8000;         // This will give me a period of 1 ms before an interrupt is requested. An interrupt will be requested when timer counts to this number.

    /** ------ Setup Timer B3 ------ **/
    // This is for PWM. Timer B3 will drive the LED rings to control brightness, and the Cue LED to make it glow.
    TB3CTL &= ~MC_3;        // Start with timer stopped. Mode referenced has no relevance to functionality, I'm just clearing the bits.
    TB3CTL |= TBSSEL_2;     // Select SMCLK source CONSIDER CHANGING THIS

    TB3CCTL1 |= OUTMOD_6 | CCIE_0;  // Set OUTMOD to Toggle/Set to output a pulse width modulated signal.
    TB3CCTL2 |= OUTMOD_6 | CCIE_0;
    TB3CCTL3 |= OUTMOD_6 | CCIE_0;
    TB3CCTL4 |= OUTMOD_6 | CCIE_0;
    TB3CCTL5 |= OUTMOD_6 | CCIE_0;  // Make sure interrupts are disabled.

    TB3CCR0 = 8000;         // f(out) = SMCLK/TB1CCR0 = frequency of 1kHz, consider this for calculating duty cycle

    TB3CCR1 = 8000;         // This determines duty cycle: DC = (1-(TBCCR1/TBCCR0))*100%, if TB1CCR1 = TB1CCR0, duty cycle is 0%.
    TB3CCR2 = 8000;
    TB3CCR3 = 8000;
    TB3CCR4 = 8000;
    TB3CCR5 = 8000;

    /** ------ Setup UART ------ **/
    UCA0CTLW0 |= UCSWRST;                      // Disable UART module and reset its registers for configuration.
    UCA0CTLW0 |= UCSSEL__SMCLK;                // Use SMCLK as source.

    // Baud Rate calculation
    // 8000000/(16*9600) = 52.083
    // Fractional portion = 0.083
    // User's Guide Table 22-4: UCBRSx = 0x49
    // UCBRFx = int ( (52.083-52)*16) = 1
    UCA0BR0 = 52;                             // 8000000/16/9600
    UCA0BR1 = 0x00;
    UCA0MCTLW = 0x4900 | UCOS16 | UCBRF_1;

    UCA0CTLW0 &= ~UCSWRST;                    // Initialize eUSCI

    //** ------ Setup Interrupts ------ **//

    UCA0IE |= UCRXIE;       // Enable USCI_A0 RX interrupt
    RTCCTL |= RTCIE;        // Enable real time clock interrupt
    P3IE   &= ~(TTL_IN);    // Disable interrupts for the incoming TTL port by default. This can be enabled later on.
    P4IE   |= BTN1;         // Enable interrupts for button 1, a test button.

    //** ------ Finish Initialization ------ **//
    TB3CTL |= MC_3;               // Start timer and start PWM, saving this for later

    SetBrightness('1', '0');      // Turn all LEDs off
    SetBrightness('2', '0');
    SetBrightness('3', '0');
    SetBrightness('4', '0');

    char int_string[5];                // Set length character array for storing user-entered integers which will be converted to integer types.
    struct LightLevel *lvl_ptr;        // Pointer for light level structure contained in arenacfgX.h.
    struct MCUinfo *dev_ptr = &Device; // Pointer to the MCUinfo structure, which contains information about the device, contained in arenacfgX.h.
    //unsigned long          RELAY_ONTIME = 500;  // Amount of time relays are set to be on.
    //unsigned long          TTL_LENGTH = 500;    // Amount of time TTLs are set to be on.
    volatile unsigned int * reg_ptr;   // A simple register pointer for dynamic register selection.
    volatile unsigned int ts_sc;       // Snapshot variable for storing the current seconds on seconds counter.
    volatile unsigned int ts_ms;       // Snapshot variable for storing the current milliseconds on milliseconds counter.
    char c, INPUT_1, INPUT_2, INPUT_3; // Single character containers for handling command inputs.

    unsigned short int  _ERROR = 0;  // Error flag.
    unsigned int             i = 0;  // Iterating variable.
    char              CCRVAL[] = ""; // Character array for handling CCR value input for PWM.
    char*               string = ""; // Character array pointer for sending messages through UART.
    unsigned int          temp = 0;  // Temporary variable for storing a previous CCR value before committing it to the light-level structure.
    unsigned short      _BLINK = 0;  // Indicates that the system must service the trial indication LED.
    unsigned short      _EXTTL = 0;  // Indicates whether or not the system will react to external TTLs.
    unsigned short      _TTLOP = 0;  // Indicates TTL operating mode. 0 for "toggle", 2 for "on request", 3 for "off"
    char           rxstring[4] = ""; // String buffer to store incoming messages from PC.
    unsigned short int  length = 4;  // Length of the string buffer. For LED commands.
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

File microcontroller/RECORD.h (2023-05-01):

/*
 * RECORD.h
 *
 *  Created on: Mar 21, 2022
 *      Author: Raquel Ibáñez Alcalá
 *      Version: v1.2 (October 6, 2022) for MCU firmware version v2.1.1 and newer
 *
 *  Library of functions, structures, and definitions made for the RECORD system at the University of Texas at El Paso, Friedman Lab.
 *
 */

#ifndef RECORD_H_
#define RECORD_H_

/* CHANGE THIS FILE ACCORDING ON WHAT ARENA YOU'RE UPDATING */
#include <mcucfg_dev1.h>

/* ----------------------------------------------------------------------------------------------------------------- */

/* ------ GPIO Definitions ------ */
// DON'T TOUCH THESE!!
// Port 1
#define RXD     BIT6    // UART RX
#define TXD     BIT7    // UART TX
#define REDLED  BIT0    // LED1 output
// Port 2
#define BTN2    BIT3    // On-board button S2 (input)
// Port 3
#define ACK     BIT0    // Acknowledge command signal (output)
#define RELAY1  BIT1    // Relay to drive larger circuit (output)
#define RELAY2  BIT2    // Relay to drive larger circuit (output)
#define RELAY3  BIT7    // Relay to drive larger circuit (output)
#define RELAY4  BIT4    // Relay to drive larger circuit (output)
#define TTL_IN  BIT5    // TTL input from Noldus, stepped down to ~ 3.3V using a voltage divider (input)
#define TTL_OUT BIT6    // TTL output to Noldus (output)
// Port 4
#define BTN1    BIT1    // On-board button S1 (input)
// Port 5
#define LED1    BIT1    // External LED
#define LED2    BIT2    // External LED
#define LED3    BIT3    // External LED
#define LED4    BIT4    // External LED
// Port 6
#define TB3_1   BIT0    // Timer 3, CCR1 output: LED ring 1
#define TB3_2   BIT1    // Timer 3, CCR2 output: LED ring 2
#define TB3_3   BIT2    // Timer 3, CCR3 output: LED ring 3
#define TB3_4   BIT3    // Timer 3, CCR4 output: LED ring 4
#define TB3_5   BIT4    // Timer 3, CCR5 output: Cue LED
#define GRNLED  BIT6    // LED2 output

/* ----------- Other ----------- */
#define MCLK_FREQ_MHZ 8 // MCLK = 8MHz, affects pulse width modulation duty cycles and baud rate for UART communication. DO NOT CHANGE.
#define delay_us(x)     __delay_cycles((long) x* 8)
#define STEP 5          // Increment value for duty cycle modulation in PWM.
#define LOWER_LIMIT 80  // Lower limit of Timer capture compare register for PWM. Used for TB3CCR5 (cue LED).
#define UPPER_LIMIT 8000// Upper limit of Timer capture compare register for PWM. Used for TB3CCR5 (cue LED).
#define DOWN 0          // Used to define a downwards direction for Timer capture compare register for PWM.
#define UP   1          // Used to define an upwards direction for Timer capture compare register for PWM.
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

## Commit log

2023-05-01 Raquel uploaded files
    Initial commit of files.
    [Basic Pillar v2.1 DWG.dwg, Basic Pillar v2.1.stl, Diagonal Floor Tile DWG.dwg, Diagonal Floor Tile.stl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]
2023-05-01 Raquel added more files
    [RATS_Schematic.brd, RATS_Schematic.sch, copper_bottom.gbr, copper_top.gbr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]
2023-05-01 Raquel added even more files
    [Dataset Column Definitions.xlsx, trial_list_example.csv]
2023-05-03 Added D's neuroeconomic analysis files
    [params_anal.xlsx]
2023-06-02 pcb/Revision 1.0/README.md created from https://stackedit.io/
2023-06-02 3d-prints/README.md created from https://stackedit.io/
2023-06-02 pcb/README.md created from https://stackedit.io/
2023-06-02 pcb/README.md updated from https://stackedit.io/

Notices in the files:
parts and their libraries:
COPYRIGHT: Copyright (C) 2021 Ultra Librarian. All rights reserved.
